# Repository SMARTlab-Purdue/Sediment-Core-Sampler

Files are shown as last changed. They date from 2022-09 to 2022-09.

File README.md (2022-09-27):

# Uncrewed Remote Underwater Robotic Sediment Core Sampler
<p align="center">
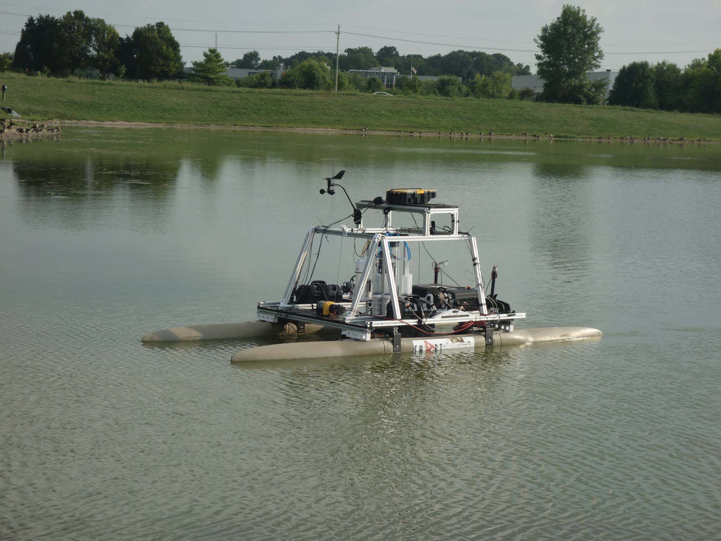
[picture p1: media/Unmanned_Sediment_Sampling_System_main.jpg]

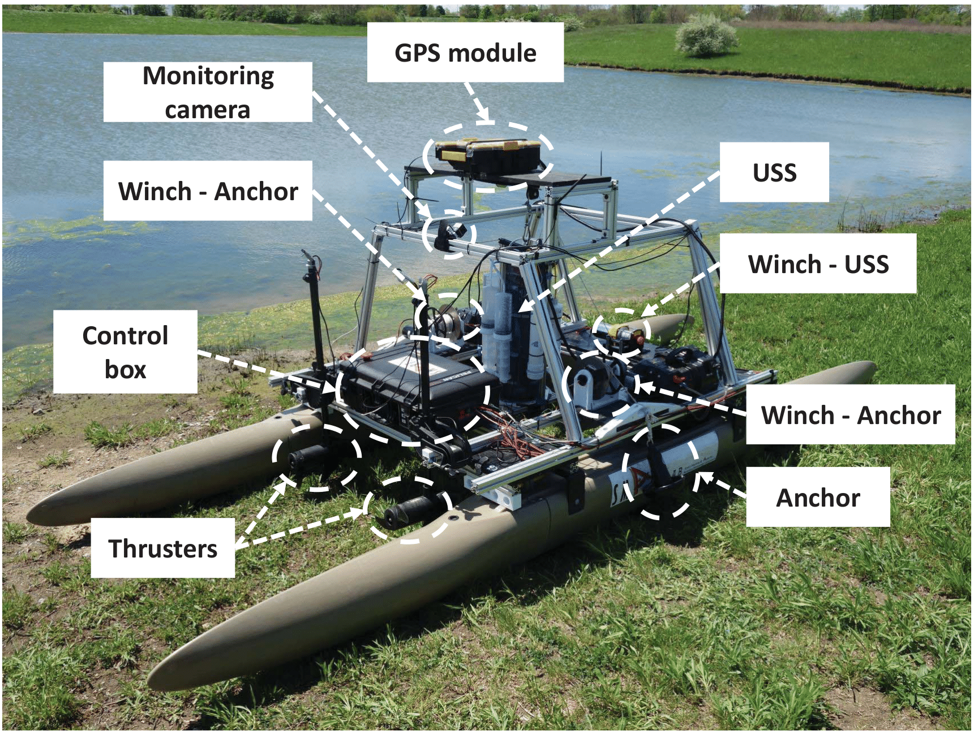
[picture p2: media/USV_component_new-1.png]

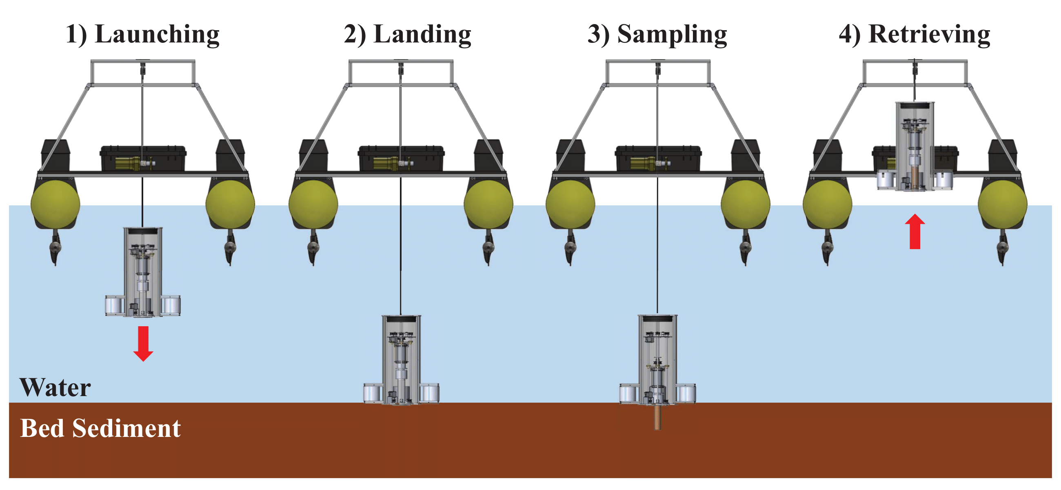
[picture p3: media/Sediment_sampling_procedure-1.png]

</p>

Sediment has a significant impact on social, economic, and environmental systems. With the need for an effective sediment management and monitoring systems growing more important, a method for precisely and reproducibly obtaining sediment samples that represent the actual environment is essential for water resource management and researchers across aquatic domains (such as lakes, rivers, reservoirs, mine drainage ponds, and wastewater lagoons). To meet this need, robotic approaches for sediment sampling have been introduced. However, they are not tailored to a sediment sampling method and do not focus on the quality of the sediment sample. In this paper, we introduce an uncrewed sediment sampling system based on the unmanned surface vehicle (USV) and underwater sediment sampler (USS) to collect sediment samples and with the ability to comprehensively study sample quality from surface-water environments. The main objective of the USV is to carry the USS to the desired sampling area and then maintain its position while launching the USS to the bottom of the body of water and sampling the sediment. The core sampling method was adopted for the USS to extend the use of the sampled sediment by minimizing the disturbance while sampling. We integrated highly flexible sediment sampling patterns and self-adaptability mechanisms to investigate the samples’ reliability and quality, and tested the effectiveness of the flexible mechanisms. Through extensive experiments, we evaluated and validated the performance of the sediment sampling system in both lab and real environments and optimized the operation of the system as a whole.

# Component List and Cost
| USV Conponent                             | Price (USD)   |
| ---------------------------------------------- | --------- |
| Nvidia Jetson Nano                             | $109.00   |
| Cytron Thruster motor driver SmartDriveDuo-30  | $150.00   |
| Two Minn kota Thrusters Model: 1352230         | $220.00   |
| Expandacraft 12 foot outrigger kit for 2 sides | $1,054.00 |
| Two tsiny DC motors for winches TS-30GZ6287    | $58.00    |
| BADLAND 2500 Lbs Utility Electric Winch        | $70.00    |
| Sparkfun Compass - HMC6352                     | $17.00    |
| Sparkfun GPS - EM506                           | $40.00    |
| USB camera ELP-USBFHD01M-L21                   | $46.00    |
| Miscellaneous                   | ~$115.00    |
| **USV Cost**                          | **$2,900.00**   |

| USS Component                                          | Price (USD) |
| ------------------------------------------------------ | ----------- |
| Two Sparkfun Pressure sensors MS5803-14BA              | $20.00      |
| testco Solenoid - 100 STA                              | $27.00      |
| Two Sparkfun Potentiometers COM-09119                  | $10.00      |
| Lipo battery 3S1P                                      | $64.00      |
| Battery volt/current sensor - Pixhawk Power Module BEC | $14.00      |
| 8'' ePlastics acrylic tube                             | $315.00     |
| Two Bluerobotics 8'' Flange WTE8-M-FLANGE-SEAL-R1-RP   | $170.00     |
| 8'' Bluerobotics cover WTE8-M-END-CAP-R1-RP            | $42.00      |
| Two Rubber bellow B01IH8JKJI                           | $40.00      |
| 3 Linear thearded rods 3313N19                         | $53.00      |
| 4 550ml syringes KIK-PLA-SYR-011                       | $56.00      |
| PVC pipes                                              | $15.00      |
| Miscellaneous                   | ~$154.00    |
| **USS Total Cost**                                         | **$1,800.00**   |
| **Platform Total Cost**                                    | **$4,700.00**   |

# Set ups

0. Set up network
 - pass: SmartROS recognizable from base station

1. main(12 V) power on; MCU 1, 2, and 3 power on
 - pass: MCU 1, 2, and 3 power/fan on

2. Nano power on
 - pass: check the green LED on

3. Arduino Mega reset
 - pass: MCU 1, 2, and 3 no blinking.
 - troubleshooting: Repeat 3 until success.

4. (from base station) ssh into nano
```
$ ssh junhan@192.168.1.4
```
 - pass: login successfully
 - troubleshooting: 192.168.1.1 -> check if nano is connected to the network; Nano's name is `junahn-desktop`

5. Sampler Controller / solenoid power on
 - pass: run the command on nano
 ```
$ ls -lha /dev/wabash_sampler
lrwxrwxrwx 1 root root 7 Mar 13 22:40 /dev/wabash_sampler -> ttyACM1
```

6. (in ssh) ros service runs okay
 - pass: the result shows Active (running)
 - troubhelshooting: sudo -i service wabashcore restart
```
$ sudo -i service wabashcore status
```
# **CHECK** If the IP address of the device changed, you have to reset the IP address.
```
$ nano setup.sh
$ source setup.sh 
```
and
```
$ systemctl status wabashcore
$ nano wabash.sh
$ sudo service wabashcore restart
```
MY_IP is the IP of the computer you run docker containers
MASTER_IP is the IP where WabashCore ROS is running (e.g., Jetson Nano) 

7. (in ssh) run source setup.sh
must run before ./run.all.sh (even if IP is not changed

8. (in ssh) launch wabash services
```
$ cd /home/junhan/repo/Codes/docker
$ ./run_all.sh
docker ps
CONTAINER ID        IMAGE               COMMAND                  CREATED             STATUS              PORTS               NAMES
97eb41a8ddde        wabash_ros          "/ros_entrypoint.sh …"   3 minutes ago       Up 3 minutes                            wabash_cam_fisheye
fb143d1255b8        wabash_ros          "/ros_entrypoint.sh …"   3 minutes ago       Up 3 minutes                            wabash_video_server
c75b6b758a35        wabash_ros          "/ros_entrypoint.sh …"   16 minutes ago      Up 16 minutes                           wabash_motor_driver
60dec6e54943        wabash_ros          "/ros_entrypoint.sh …"   16 minutes ago      Up 16 minutes                           wabash_distance_traveled
3dc0acf10f40        wabash_ros          "/ros_entrypoint.sh …"   16 minutes ago      Up 16 minutes                           wabash_solenoid_controller
191ef87043a8        wabash_ros          "/ros_entrypoint.sh …"   16 minutes ago      Up 16 minutes                           wabash_rotary_controller
1329ad7e1d2f        wabash_ros          "/ros_entrypoint.sh …"   16 minutes ago      Up 16 minutes                           wabash_sampler_serial
+ PRESSURE_DEPTH!!!
+ GPS!!!!
$ rostopic list (you should see many topics there!)
```

9. run UI on the base station
```
$ ./ui.run 192.168.1.3
$ cd /storage/
$ python3 ui.py
 - pass: you see the UI
 - troubleshooting: you may need to make the terminal full size
```

10. (in ssh) record the experiment
```
$ ./record.sh
Ctrl + C to stop
$ ls -lha 
2021-03-13-23-46-43.bag .....
```
11. (in base station) open browser (i.e. Chrome) to monitor USV via fisheye camera (use Jetson IP)

192.168.1.6:8080

12-a. (in another ssh) send out the USV manually
```
$ rosrun teleop_twist_keyboard teleop_twist_keyboard.py
```
press 'q' button to increase the speed
press 'z' button to decrease the speed
speed: 1 turn: 2 - max. performance of the thruster

12-b. (in another ssh) send out the USV in auto mode
```
$ cd /home/junhan/repo/Codes/docker/usv_autopilot
$ lat=LATITUDE lon=LONGITUDE ./auto.sh
Setting the autopilot to a coordinate: LATITUDE, LONGITUDE
+ rostopic pub -1 /usv/autopilot/cmd/engage std_msgs/Bool True
publishing and latching message for 3.0 seconds
+ rostopic pub -1 /usv/autopilot/destination sensor_msgs/NavSatFix '{latitude: LATUTUDE, longitude: LONGITUDE}'
publishing and latching message for 3.0 seconds
Done
+ set +x
```

11-c. killing autopilot in case of emergency
```
$ cd /home/junhan/repo/Codes/docker/usv_autopilot
$ ./kill.sh
Attempting to kill autopilot...
+ rostopic pub -1 /usv/autopilot/cmd/kill std_msgs/Bool True
publishing and latching message for 3.0 seconds
+ set +x
```

# How to Reset OpenCR board
```
$ rostopic pub -1 /sampler/reset std_msgs/Byte 0x00
```

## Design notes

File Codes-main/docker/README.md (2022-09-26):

## Dockerized ROS Services

To build Wabash ROS image in Docker,
```
$ ./build.sh
```

To run ROS core,
```
$ ./core.run
```

## Wabash services

To run the Wabash services,
```
# this requires the OpenCR connected
$ ./run_all.sh
```

To clean them up,
```
$ ./clean.sh
```

## Camera Streaming

To run camera streaming,
```
$ cp camera.run camera_left.run
$ nano camera_left.run
# modify IP to the IP address of the node on which core.run runs and NAME
# DEVICE should be the path of the camera (which might be mapped to /dev/wabash_cam_*
$ ./camera_left.run
```

To run web video service,
```
$ nano video_server.run
# modify IP to the IP address of the node on which core.run runs
$./video_server.run
```

On remote (base station) open a browser (Chrome is recommended) and type
```
# replace IP with the actual IP address of the core node
http://IP:8080
```

Finally, click the camera you want to open.

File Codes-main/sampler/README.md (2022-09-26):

## Sampler Firmware

[firmware.ino](firmware.ino) is the firmware for sadiment sampler board (OpenCR).

The code uses ROS topics to publish and subscribe messages. Available topics are,

- ...

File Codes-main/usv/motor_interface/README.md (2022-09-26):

# Arduino Mega for Interfacing with Motor drivers

An arduino mega is used to bridge interfaces between SmartDriveDuo-30/60 and Jetson.

## Commands
- `th [l, r] INT`: change direction/velocity of left/right thrusters
- `an [l, r] INT`: change direction/velocity of left/right anchors
- `sa [l, r] INT`: change direction/velocity of left/right sampler
__NOTE: only `r` is used__
- `cll [on, off]`: change on/off of left clutch
- `clr [on, off]`: change on/off of right clutch
- `cl [on, off]`: change on/off of sampler clutch
- `init`: send the init signal to the motor drivers

## Clutch Pins
```
uint8_t clutch_sampler_pin = 2;
uint8_t clutch_left_pin = 3;
uint8_t clutch_right_pin = 4;
```

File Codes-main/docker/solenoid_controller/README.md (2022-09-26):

# Solenoid Controller

`/sampler/cmd/solenoid`: float32 solenoid toggle interval in seconds; sending 0. to stop.

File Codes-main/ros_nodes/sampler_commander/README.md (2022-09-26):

# Sampler Commander

Sampler commander is a ROS node that takes commands from the base station. Its job is to convert high-level commands, e.g., "initiate sampler" into a corresponding set of commands that are executable by the sampler board.

## Commands

- init sampler: initializes the sampler

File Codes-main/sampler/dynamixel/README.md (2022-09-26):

# Dynamixel MX-64AR

## Modes

NOTE: [Reference](http://wiki.ros.org/dynamixel_controllers/Tutorials/SettingUpDynamixel)

Joint mode: position to given angle and hold

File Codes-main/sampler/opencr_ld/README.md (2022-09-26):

# OpenCR flashing on Jetson

Use the opencr_ld binary to flash firmware to OpenCR board

```
$ export OPENCR_PORT=/dev/ttyACM0
$ binary_arm64/opencr_ld ${OPENCR_PORT} 115200 /PATH/TO/FIRMWARE.bin 1
opencr_ld ver 1.0.4
opencr_ld_main 
>>
file name : /home/smartlab/sampler/firmware.ino.bin 
file size : 175 KB
Open port OK
Clear Buffer Start
Clear Buffer End
Board Name : OpenCR R1.0
Board Ver  : 0x17020800
Board Rev  : 0x00000000
>>
flash_erase : 0 : 1.079000 sec
flash_write : 0 : 0.995000 sec 
CRC OK 10C7CE4 10C7CE4 0.006000 sec
[OK] Download 
jump_to_fw 
jump finished
```

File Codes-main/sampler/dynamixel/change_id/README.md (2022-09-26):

# Change ID of Dynamixel

[change_id.ino](change_id.ino) changes ID of a connected Dynamixel. The new ID is in the code. The linear motion motor should be assigned ID 1 and rotation motor should be assigned ID 2.

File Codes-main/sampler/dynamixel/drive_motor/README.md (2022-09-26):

# Test Linear Dynamixel

[motor.ino](motor.ino) accepts a float value to drive Dynamixel ID 1 motor at the desired speed. The value is fed with the unit of m/s.

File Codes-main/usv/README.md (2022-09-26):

# Jetson Nano for USV

## Camera setup

```
# on sudo
$ cat /etc/udev/rules.d/10-wabash.rules 
SUBSYSTEM=="tty" ATTRS{idProduct}=="0042", ATTRS{idVendor}=="2341", ATTRS{manufacturer}=="Arduino*", SYMLINK+="wabash_motor_driver"
SUBSYSTEM=="tty" ATTRS{idProduct}=="5740", ATTRS{idVendor}=="0483", ATTRS{manufacturer}=="ROBOTIS", SYMLINK+="wabash_sampler"
SUBSYSTEM=="tty" ATTRS{idProduct}=="0043", ATTRS{idVendor}=="2341", SYMLINK+="wabash_gps"
SUBSYSTEM=="tty" ATTRS{idProduct}=="xxxx", ATTRS{idVendor}=="yyyy", SYMLINK+="wabash_pressure"

SUBSYSTEM=="video4linux", KERNEL=="video[0-9]*", ATTRS{idVendor}=="05a3", ATTRS{idProduct}=="9420", ATTRS{devpath}=="2.1", SYMLINK+="wabash_cam_left"
SUBSYSTEM=="video4linux", KERNEL=="video[0-9]*", ATTRS{idVendor}=="05a3", ATTRS{idProduct}=="9420", ATTRS{devpath}=="2.2", SYMLINK+="wabash_cam_right"
SUBSYSTEM=="video4linux", KERNEL=="video[0-9]*", ATTRS{idVendor}=="05a3", ATTRS{idProduct}=="9422", SYMLINK+="wabash_cam_fisheye_other"
SUBSYSTEM=="video4linux", KERNEL=="video[0-9]*", ATTRS{idVendor}=="32e4", ATTRS{idProduct}=="9230", SYMLINK+="wabash_cam_fisheye"
SUBSYSTEM=="video4linux", KERNEL=="video[0-9]*", ATTRS{idVendor}=="534d", ATTRS{idProduct}=="2109", SYMLINK+="wabash_cam_sampler"
(add more camera here)

sudo -i udevadm control --reload-rules 
sudo -i udevadm trigger 
ls -lh /dev/wabash*
```

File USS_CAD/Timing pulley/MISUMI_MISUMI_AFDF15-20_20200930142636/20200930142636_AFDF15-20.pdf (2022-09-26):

## Backside Tension Idler Pulley - Both Sides Bearing (MISUMI)

Part Number AFDF15-20 | 20200930142636
Type | Idlers | Belt Widt h Used(Inch)(Inch) | 0.37 in (3/8")
Belt Widt h Used(mm)(mm) | 10 | Ma t eria l | [Aluminum] Aluminum Alloy 2000 series
Surf a ce Trea t ment | Clear Anodize | O.D.(mm) | 20
Timing Pulleys/Idlers | Idlers | Bea ring Position | -
Groove Widt h W(mm) | 15 | Wit h or w/o Flange | Provided

Copyright © MISUMI Corporation All Rights Reserved.

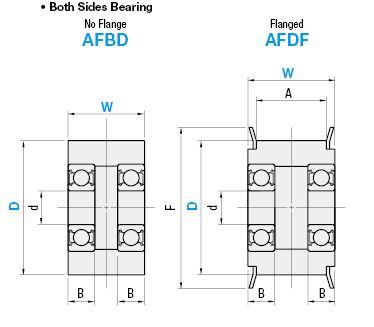
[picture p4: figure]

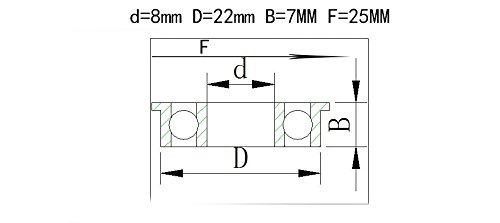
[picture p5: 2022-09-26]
USS_CAD/Ball bearing/Flange Ball Bearing F608ZZ 8x22x7 mm.jpg

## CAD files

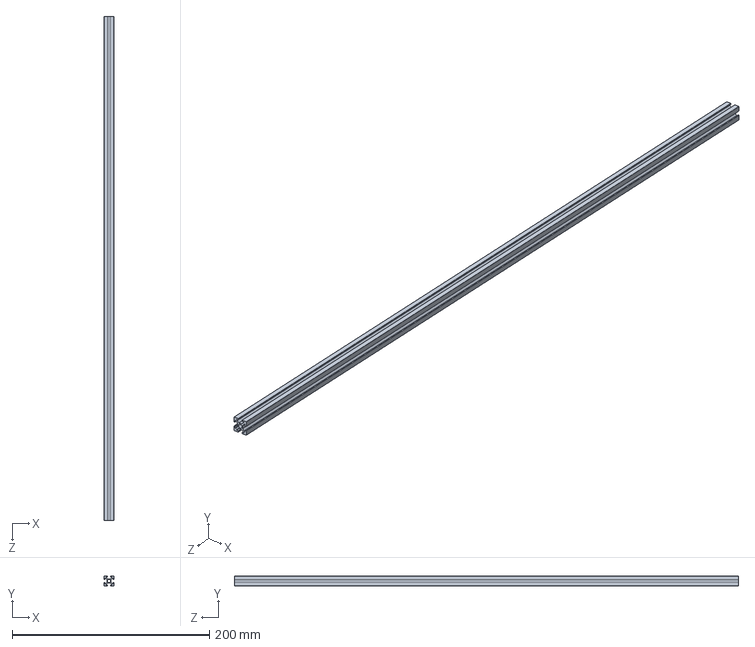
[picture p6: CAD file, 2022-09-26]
USS_CAD/Al beam_10mm_main.SLDPRT
10.0 x 10.0 x 511.0 mm

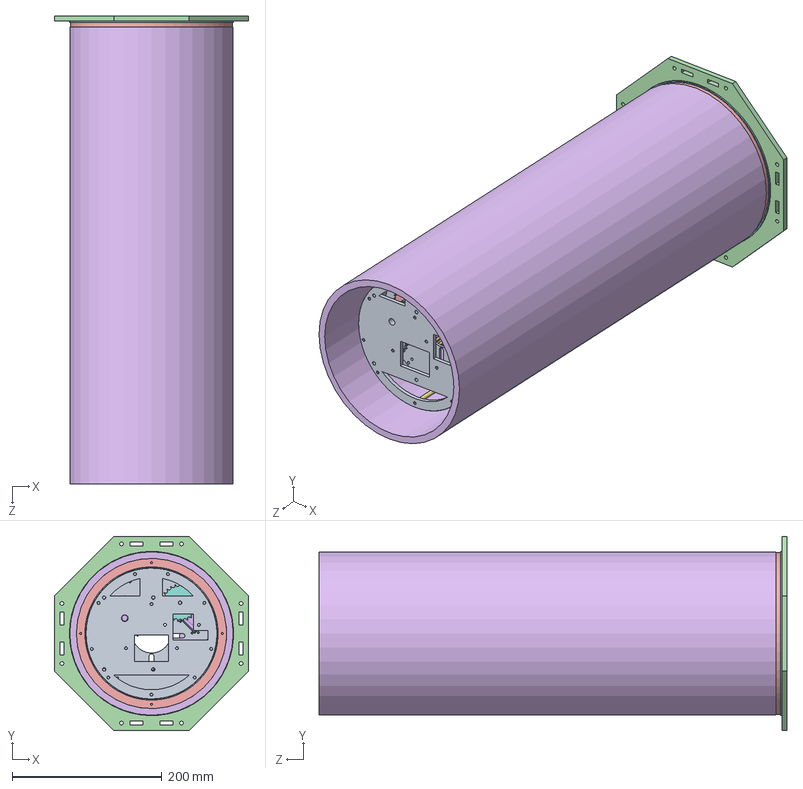
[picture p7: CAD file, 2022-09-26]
USS_CAD/Assembly/Sampler_Guide_new_2.SLDASM
259.0 x 259.0 x 624.3 mm
Top plate
Bearing mount_Top plate_new_2 x 3
8mm Lead Screw_MTSBRW8-490-F6-V6-S30-Q6 x 3
Flange Ball Bearing F608ZZ 8x22x7 mm x 2
2302K530_MACHINABLE-BORE SPROCKET
MX-64AT_AR
Timing pulley mount_MX64AR_new_3
2302K520_MACHINABLE-BORE SPROCKET
Electrics plate_new_2
Al beam_10mm_main x 3
Bearing mount_Bottom plate_new_ver.3 x 2
Bottom plate
M3x50 Spacer Round Column x 3
Rubber gasket_2mm
2302K430_MACHINABLE-BORE SPROCKET x 3
2302K430_MACHINABLE-BORE SPROCKET_8mm bore
8mm bearing mount_gear set
1mm spacer
3mm spacer
Core_Big bellow mount_bottom

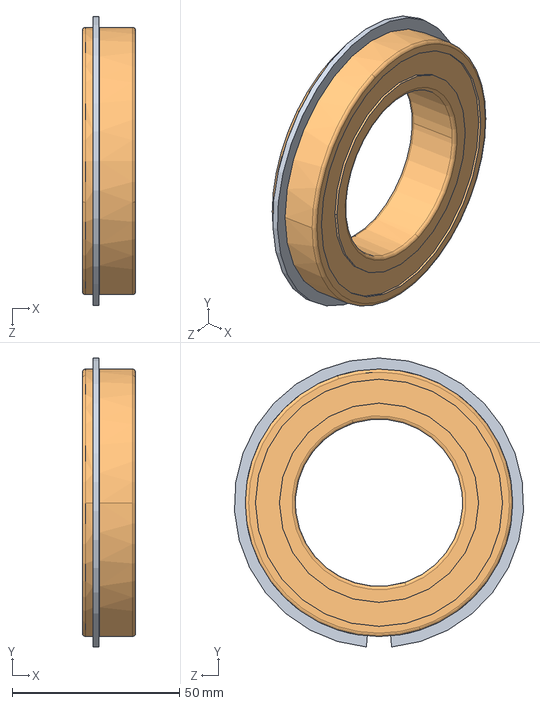
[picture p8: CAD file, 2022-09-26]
USS_CAD/Ball bearing/f608zz-flange-ball-bearing-1.snapshot.3/B6010ZZNR_SolidWorks_Native)_=2006_20200910/SOLIDWORKS/B6010ZZNR.sldasm
16.0 x 86.4 x 86.5 mm
B6010ZZNR_3
B6010ZZNR_5

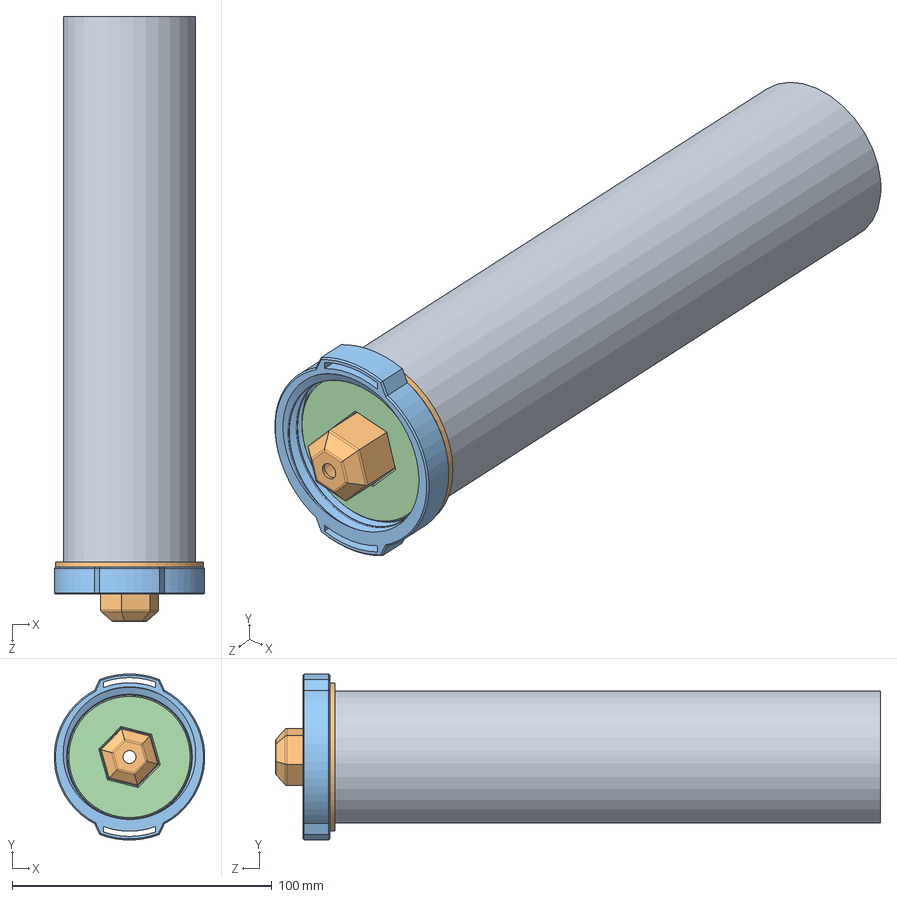
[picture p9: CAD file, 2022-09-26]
USS_CAD/Core mount/Core.SLDASM
57.9 x 63.9 x 233.0 mm
Sampling core liner
Core_Core mount_checkvv mount.stp
core core mount fastener.stp
Core_Core_mount_fastener_holder.stp

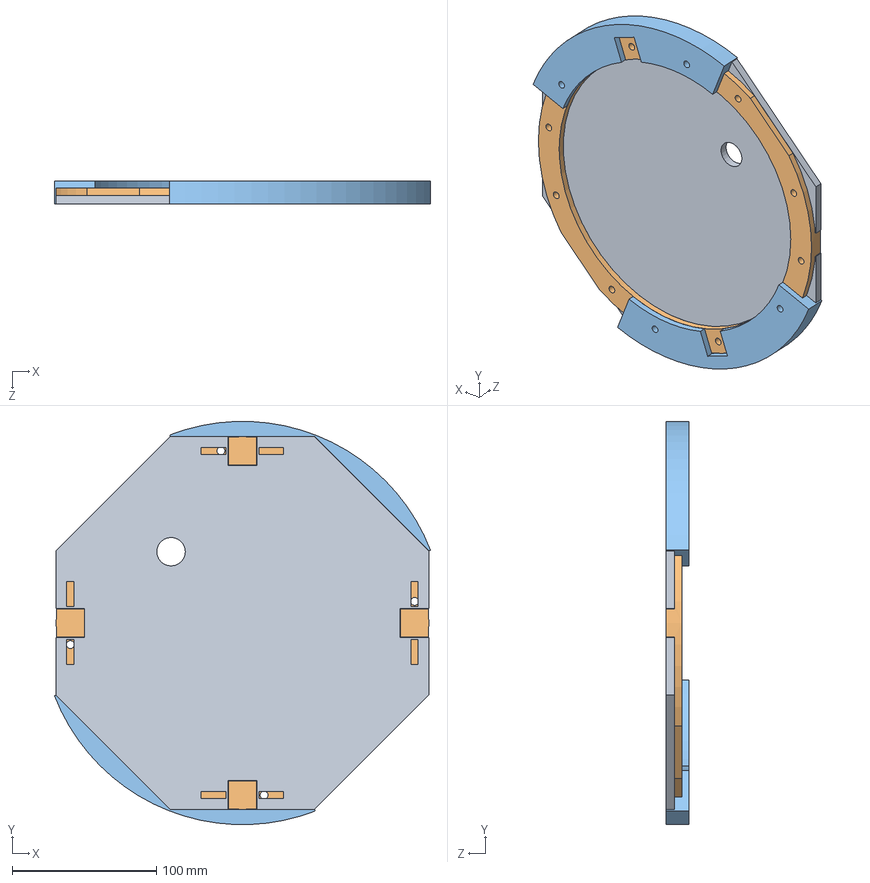
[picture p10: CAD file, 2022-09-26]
USS_CAD/External frame/External frame mount.SLDASM
261.1 x 279.8 x 16.1 mm
Top cover_2
External frame mount_ring
External frame mount_ring_parts x 2

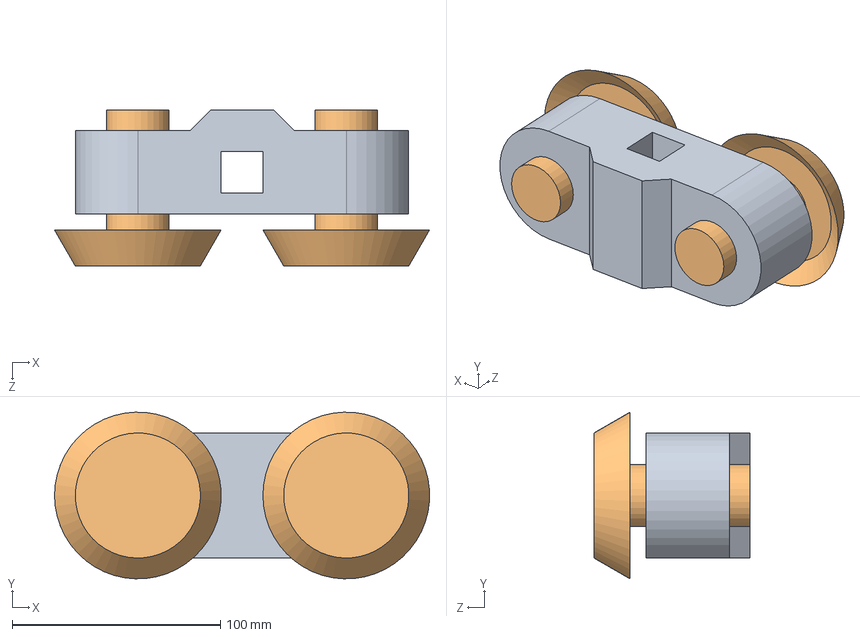
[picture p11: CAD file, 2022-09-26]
USS_CAD/Landing gear/Landing gear_concept_3.SLDASM
179.9 x 80.0 x 75.0 mm
Landing gear_concept_3_part1
Landing gear_concept_3_part2 x 2

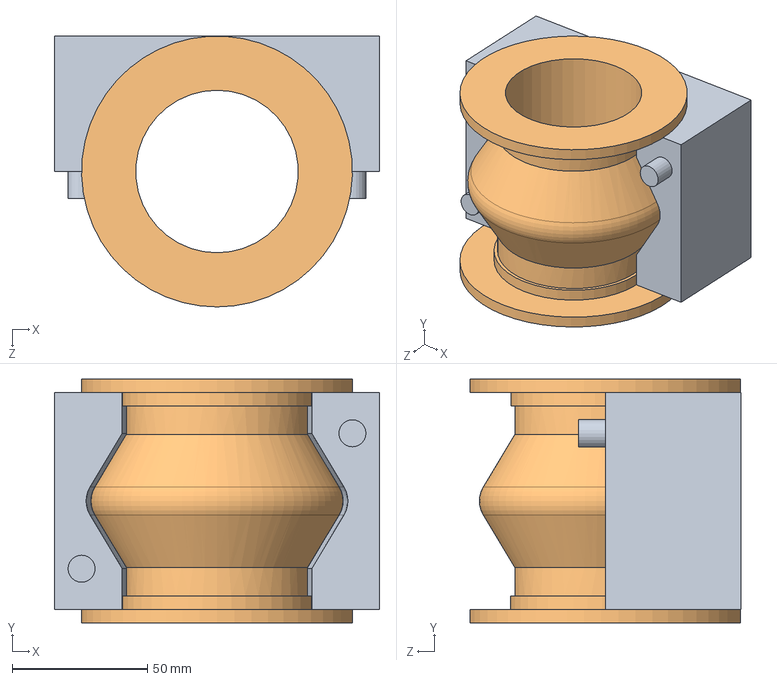
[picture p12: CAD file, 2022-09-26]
USS_CAD/Rubber bellow/Small bellow.SLDASM
120.0 x 90.0 x 100.0 mm
Small bellow mold_bottom
Small bellow mold_core

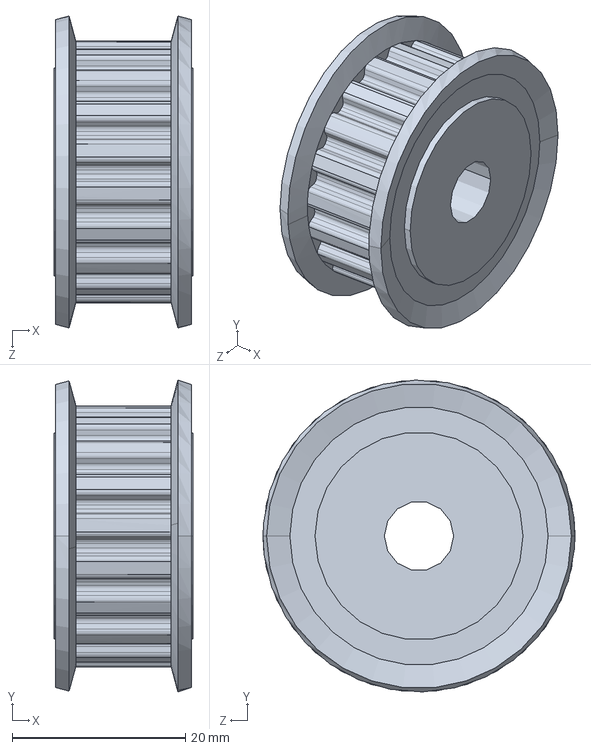
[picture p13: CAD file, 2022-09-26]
USS_CAD/Timing pulley/SOLIDWORKS/ATP19XL037_A_H8.sldasm
16.0 x 36.0 x 36.0 mm

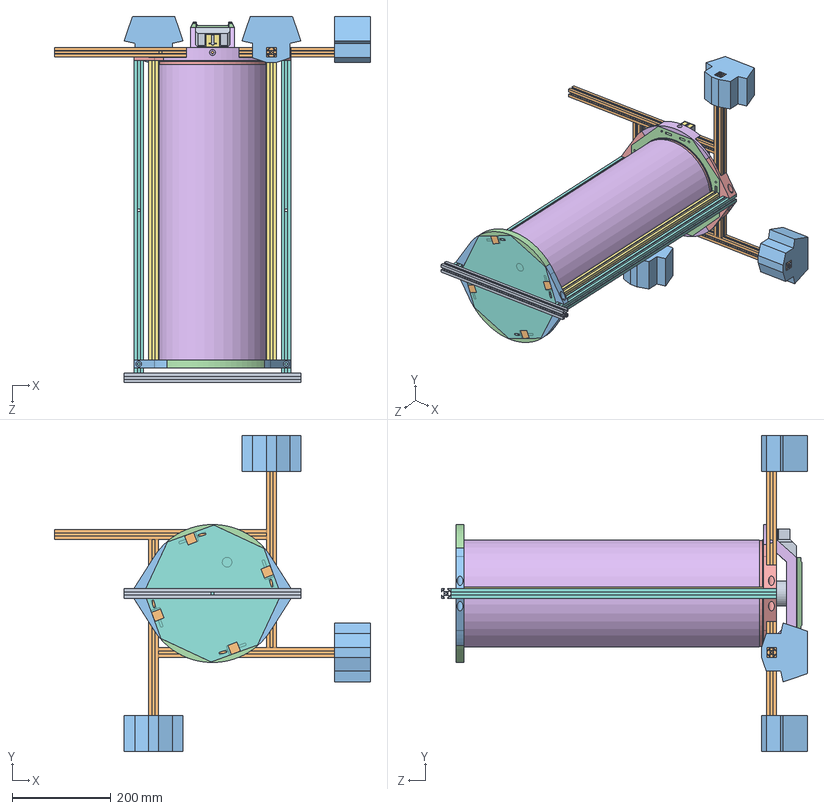
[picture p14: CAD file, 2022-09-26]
USS_CAD/Assembly/Sampler_Assemble_External Frame_properties.SLDASM
641.0 x 641.0 x 743.4 mm
Top plate
Bearing mount_Top plate_new_2 x 3
8mm Lead Screw_MTSBRW8-490-F6-V6-S30-Q6 x 3
Flange Ball Bearing F608ZZ 8x22x7 mm x 3
2302K530_MACHINABLE-BORE SPROCKET
MX-64AT_AR x 2
Timing pulley mount_MX64AR_new_3
2302K520_MACHINABLE-BORE SPROCKET
Electrics plate_new_2
Al beam_10mm_main
Bearing mount_Bottom plate_new_ver.3 x 3
Bottom plate
WTE8-M-FLANGE-SEAL-R1
8'' PVC pipe
M3x50 Spacer Round Column
Rubber gasket_2mm
2302K430_MACHINABLE-BORE SPROCKET x 3
2302K430_MACHINABLE-BORE SPROCKET_8mm bore
8mm bearing mount_gear set
1mm spacer
3mm spacer
Core_Big bellow mount_bottom
Core_Plate_new
Motor mount_core plate_rev.2
Timing pulley mount_MX64AR_new_2
2302K430_MACHINABLE-BORE SPROCKET_MX64AR
Core_Connector_top
Torque sensor_bottom
Core_Main cover_new_potentiometer
Core_Solenoid mount_potentiometer
Core_Core mount_top_potentiometer
Core_Connector_core,solenoid
Core_Core mount_bottom
1885N160_SPRING-LOADED ROTARY SHAFT SEAL
Core_Connector_bottom_b
Core_Connector_bottom_t
Core_Small bellow mount_bottom
Core_Small bellow mount_top
MTSFR8.par x 3
2302K530_MACHINABLE-BORE SPROCKET_Torque sensor
Sampling core liner
Core_Core mount_checkvv mount.stp
core core mount fastener.stp
Core_Core_mount_fastener_holder.stp
Small Bellow
Core_Big bellow mount_top
2302K430_MACHINABLE-BORE SPROCKET_idler_6mm x 2
Top cover_2 x 2
Big Bellow
External frame mount_ring
External frame mount_ring_part_2_outer frame x 2
External frame mount_ring_parts x 2
External frame mount_ring_parts_bottom mount_outer frame x 2
External frame mount_ring_parts_bottom mount x 2
Al extrusion_short x 2
Al extrusion_tall x 2
Al extrusion_top bar
Al extrusion(20x20x430) x 4
Lead mount_final x 2
gate guide.stp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

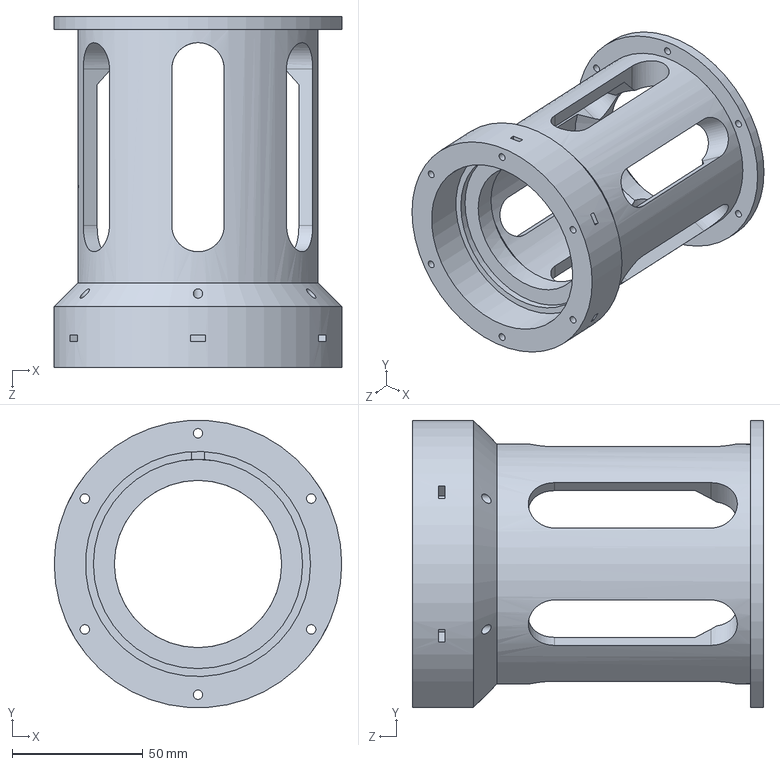
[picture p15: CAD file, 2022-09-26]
USS_CAD/Core_Main cover.SLDPRT
110.0 x 109.9 x 134.3 mm

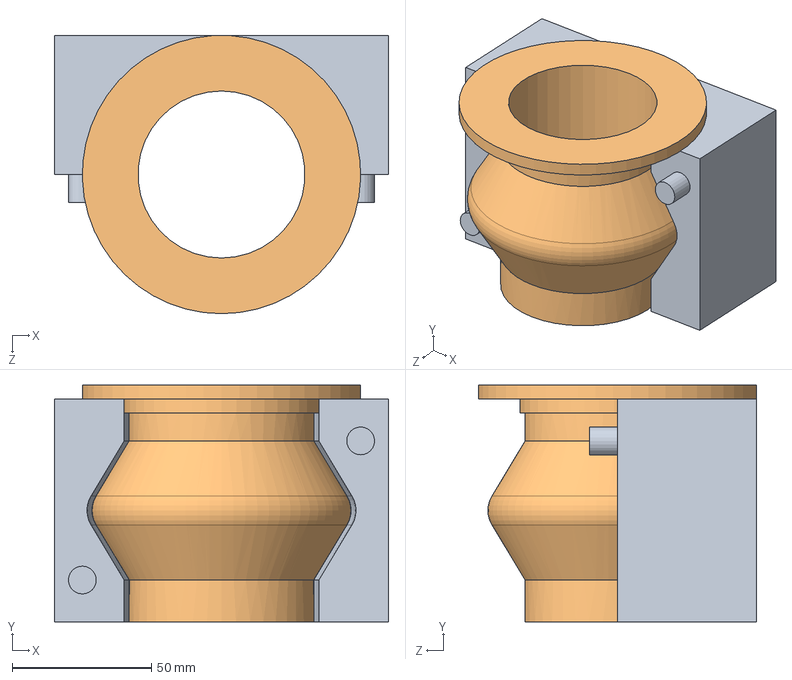
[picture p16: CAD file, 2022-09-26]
USS_CAD/Rubber bellow/Small bellow casting_2.SLDASM
120.0 x 85.0 x 100.0 mm
Small bellow mold_bottom
Small bellow mold_core_new_1

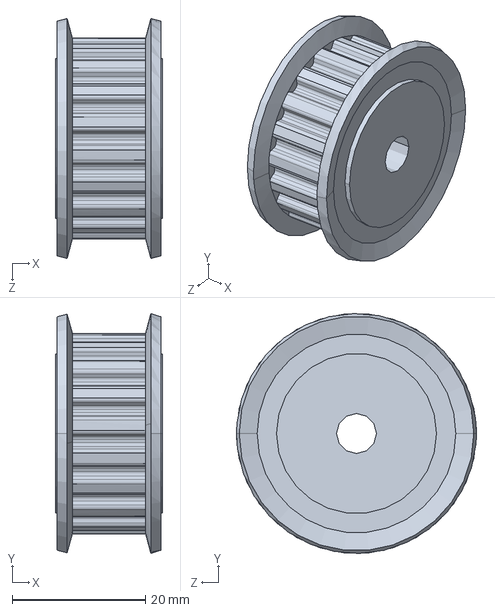
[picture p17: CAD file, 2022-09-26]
USS_CAD/Timing pulley/SOLIDWORKS/ATP19XL037_A_H6.sldasm
16.0 x 36.0 x 36.0 mm

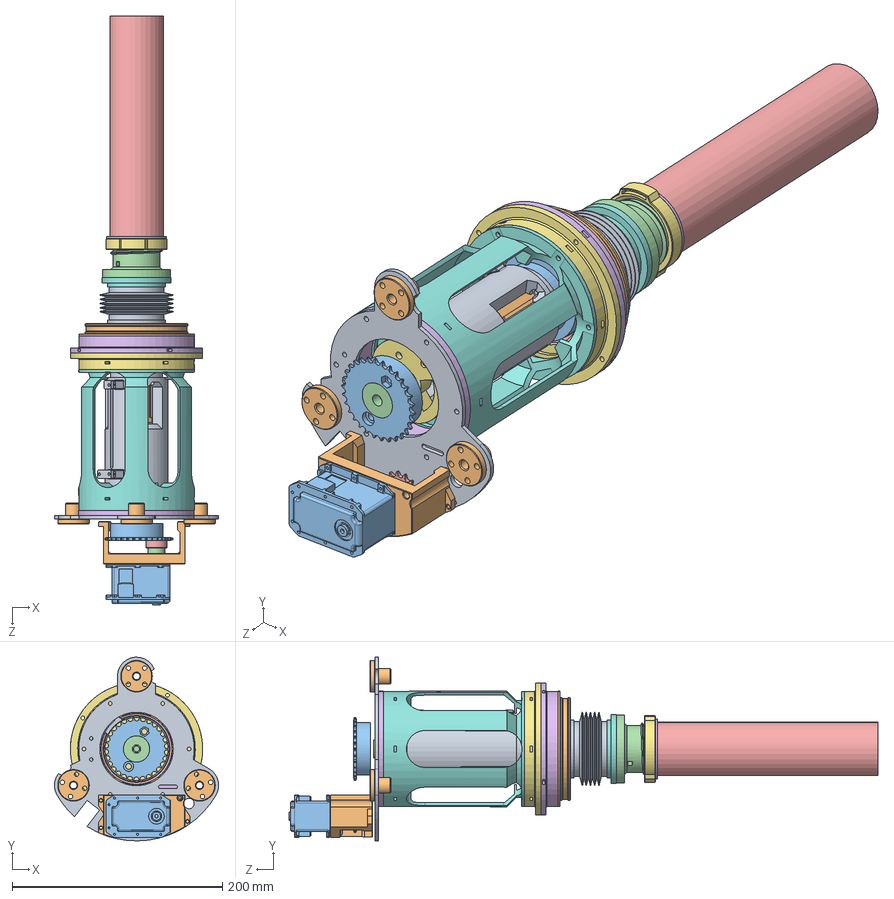
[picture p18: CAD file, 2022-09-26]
USS_CAD/Assembly/Sampler_Core_new.SLDASM
156.4 x 175.0 x 560.7 mm
Core_Plate_new
Motor mount_core plate_rev.2
MX-64AT_AR
Timing pulley mount_MX64AR_new_2
2302K430_MACHINABLE-BORE SPROCKET_MX64AR
Core_Connector_top
Torque sensor_bottom
Core_Main cover_new_potentiometer
Core_Solenoid mount_potentiometer
Core_Core mount_top_potentiometer
Core_Connector_core,solenoid
Core_Core mount_bottom
1885N160_SPRING-LOADED ROTARY SHAFT SEAL
Core_Connector_bottom_t
Core_Small bellow mount_bottom
Core_Small bellow mount_top
MTSFR8.par x 3
2302K530_MACHINABLE-BORE SPROCKET_Torque sensor
Flange Ball Bearing F608ZZ 8x22x7 mm
Sampling core liner
Core_Core mount_checkvv mount.stp
core core mount fastener.stp
Core_Core_mount_fastener_holder.stp
Small Bellow
Core_Big bellow mount_top

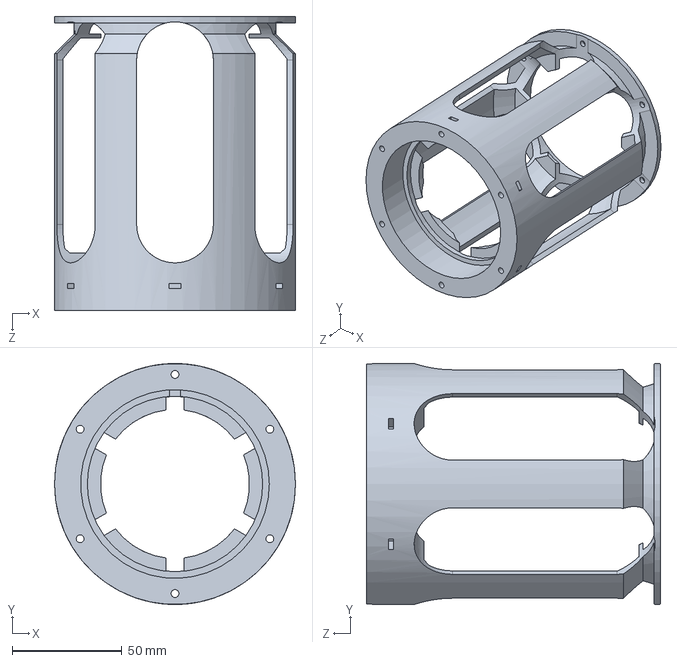
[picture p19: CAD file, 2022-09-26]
USS_CAD/Core_Main cover_new_potentiometer.SLDPRT
110.0 x 110.0 x 134.3 mm

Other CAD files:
USS_CAD/Ball bearing/B6010ZZNR_SolidWorks_Native)_=2006_20201014/SOLIDWORKS/B6010ZZNR.sldasm
USS_CAD/Timing pulley/SOLIDWORKS/ATP19XL037_A_H8_QTC16_M3.sldasm
USS_CAD/Assembly/Sampler_Assemble_External Frame.SLDASM
USS_CAD/Assembly/Sampler_Assemble.SLDASM
USS_CAD/1885N160_SPRING-LOADED ROTARY SHAFT SEAL.SLDPRT
USS_CAD/3mm spacer.SLDPRT
USS_CAD/8_ PVC pipe.SLDPRT
USS_CAD/8_ PVC pipe_property.SLDPRT
USS_CAD/8mm shaft_hollow_56.7.SLDPRT
USS_CAD/Al extrusion(20x20x150).SLDPRT
USS_CAD/Al extrusion(20x20x430).SLDPRT
USS_CAD/Al extrusion(20x20x615.6).SLDPRT
USS_CAD/Assembly/Old/MX64AR mount.SLDASM
USS_CAD/Assembly/Old/Motor unit_core plate.SLDASM
USS_CAD/Assembly/Old/Sampler_Core.SLDASM
USS_CAD/Assembly/Old/Sampler_Guide.SLDASM
USS_CAD/Assembly/Old/Sampler_Guide_new.SLDASM
USS_CAD/Assembly/Old/Sampler_Test_1.SLDASM
USS_CAD/Assembly/Old/Sampler_Test_1_1.SLDASM
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

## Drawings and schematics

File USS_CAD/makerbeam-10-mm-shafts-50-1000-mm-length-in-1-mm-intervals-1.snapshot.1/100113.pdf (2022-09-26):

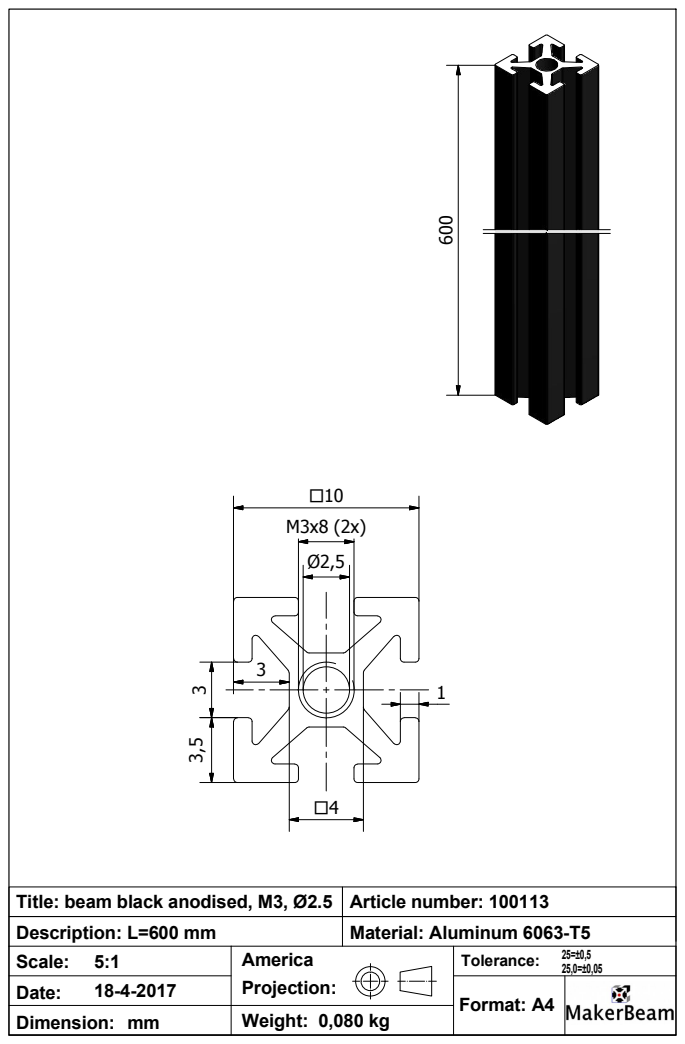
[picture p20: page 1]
America; Weight: 0,080 kg; 25=±0,5 Scale:; Date:; Dimension: mm; Format: A4; Tolerance:; Article number: 100113; Description: L=600 mm; Material: Aluminum 6063-T5; Projection:

Title: beam black anodised, M3, Ø2.5

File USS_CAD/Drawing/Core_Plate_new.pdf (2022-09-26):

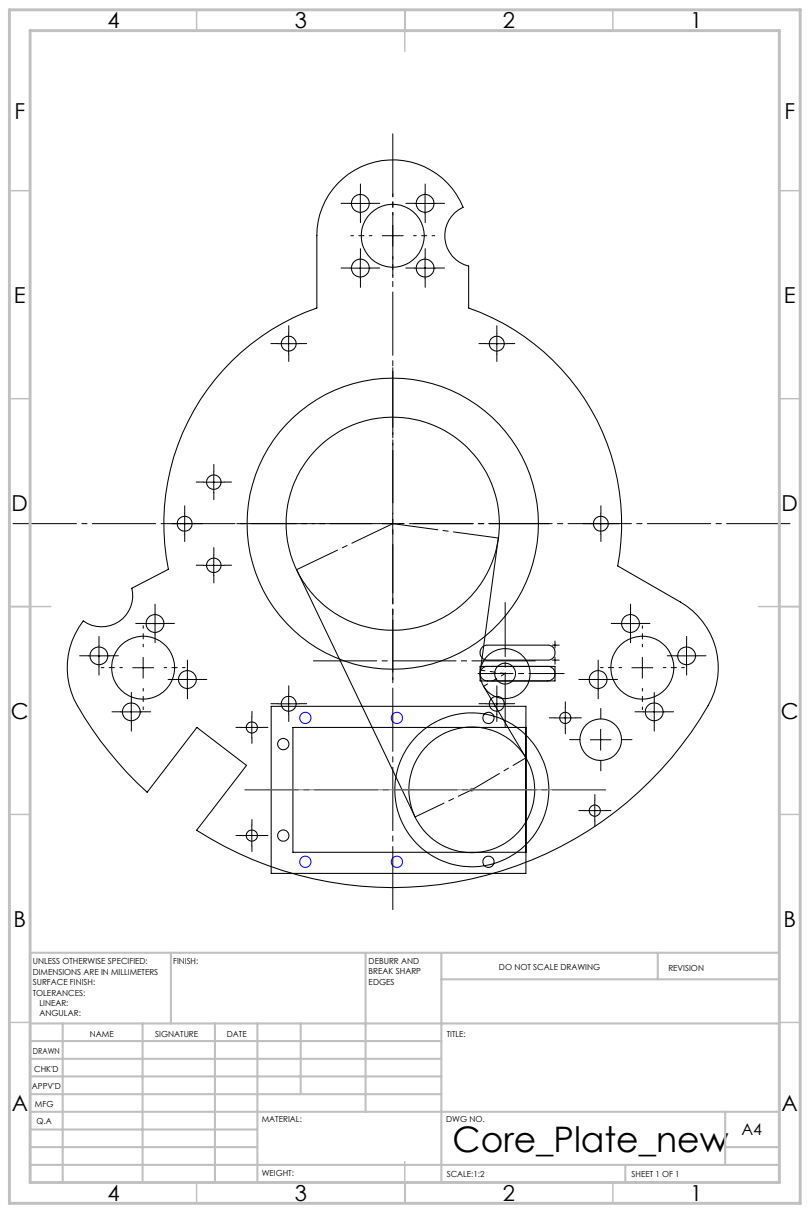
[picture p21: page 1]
FINISH:; DEBURR AND; BREAK SHARP; DO NOT SCALE DRAWING; REVISION; SCALE:1:2; SHEET 1 OF 1

UNLESS OTHERWISE SPECIFIED:
DIMENSIONS ARE IN MILLIMETERS
SURFACE FINISH:
TOLERANCES:
LINEAR:
ANGULAR:

NAME | SIGNATURE | DATE | | | | TITLE:

DRAWN
CHK'D
APPV'D
MFG
Q.A | | | | MATERIAL: | DWG NO. Core_Plate_new | A4

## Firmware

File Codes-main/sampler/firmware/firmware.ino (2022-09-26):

/*******************************************************************************
* Copyright 2016 ROBOTIS CO., LTD.
*
* Licensed under the Apache License, Version 2.0 (the "License");
* you may not use this file except in compliance with the License.
* You may obtain a copy of the License at
*
*     http://www.apache.org/licenses/LICENSE-2.0
*
* Unless required by applicable law or agreed to in writing, software
* distributed under the License is distributed on an "AS IS" BASIS,
* WITHOUT WARRANTIES OR CONDITIONS OF ANY KIND, either express or implied.
* See the License for the specific language governing permissions and
* limitations under the License.
*******************************************************************************/

/* Authors: Yoonseok Pyo, Leon Jung, Darby Lim, HanCheol Cho */


#include <ros.h>
#include <sensor_msgs/Imu.h>
#include <std_msgs/Byte.h>

#include <std_msgs/Float32.h>
#include <std_msgs/Int32.h>

#include <tf/tf.h>
#include <tf/transform_broadcaster.h>

#include <IMU.h>

#include <SPI.h>

//#include <Wire.h>
//#include <SparkFun_MS5803_I2C.h> // Click here to get the library: http://librarymanager/All#SparkFun_MS5803-14BA

//MS5803 sensor(ADDRESS_HIGH);

#include <DynamixelWorkbench.h>

#if defined(__OPENCM904__)
  #define DEVICE_NAME "3" //Dynamixel on Serial3(USART3)  <-OpenCM 485EXP
#elif defined(__OPENCR__)
  #define DEVICE_NAME ""
#endif

#define BAUDRATE  57600
#define STALL_CURRENT 4100 // Stall current mA
#define DXL_ID_1  1
#define DXL_ID_2  2

#define SPI_MAX_speed 500000
SPISettings set1(SPI_MAX_speed, MSBFIRST, SPI_MODE0);
#define SDADtransmission 0xA6
#define SDADstatus 0xF5

#define ENCODER_PIN 8
#define RESOLUTION 40

DynamixelWorkbench dxl_wb;


float DXL_ID_1_Present_Velocity = 0;
int32_t DXL_ID_1_Present_Position, DXL_ID_2_Present_Position;
float DXL_ID_1_Current, DXL_ID_2_Current;

int16_t potentiometer_linear_pin = A0;
int16_t potentiometer_rotary_pin = A2;

// Magnetic encoder linear CS pin
uint8_t encoder_linear_cs=9;
// Magnetic encoder rotary CS pin
uint8_t encoder_rotary_cs=10;

#define STRING_BUF_NUM 64
String pressure_reading[STRING_BUF_NUM];
// bool is_new_upper_pressure = false;
// bool is_new_lower_pressure = false;

//Reset pin
int Reset = 12;

// Encoder counter
unsigned long gulCount = 0;
unsigned long gulStart_Timer = 0;

// Indicators for upper and lower limit switches
uint8_t is_upper_limit_pressed = 0;
uint8_t is_lower_limit_pressed = 0;

// When upper limit switch is pressed
// stage 0: Move linear motor down at full speed for a second
// stage 1: Stop the linear motor
uint32_t emergency_upper_limit_stage1;

// When lower limit switch is pressed
// stage 0: Stage rotary motor to center and move linear motor up for a second
// stage 1: Stop the linear motor
// stage 2: Move linear motor up (to the top)
uint32_t emergency_lower_limit_stage1;
uint32_t emergency_lower_limit_stage2;


ros::NodeHandle nh;

/*******************************************/
// Publisher Parts
/*******************************************/
//Pub_MOTORS
std_msgs::Float32 dx_1_read_current_velocity_msg;
ros::Publisher pub_dx_1_velocity_read("sampler/motor/linear/read_velocity", &dx_1_read_current_velocity_msg);
std_msgs::Int32 dx_1_read_current_position_msg;
ros::Publisher pub_dx_1_position_read("sampler/motor/linear/read_position", &dx_1_read_current_position_msg);
std_msgs::Float32 dx_1_read_current_msg;
ros::Publisher pub_dx_1_current_read("sampler/motor/linear/current", &dx_1_read_current_msg);
std_msgs::Int32 dx_2_read_current_position_msg;
ros::Publisher pub_dx_2_position_read("sampler/motor/rotary/read_position", &dx_2_read_current_position_msg);
std_msgs::Float32 dx_2_read_current_msg;
ros::Publisher pub_dx_2_current_read("sampler/motor/rotary/current", &dx_2_read_current_msg);


//Pub_IMU
sensor_msgs::Imu imu_msg;
ros::Publisher imu_pub("sampler/imu", &imu_msg);
geometry_msgs::TransformStamped tfs_msg;
tf::TransformBroadcaster tfbroadcaster;
cIMU imu;

//Pub_MAGNETIC_ENCODER_LINEAR
std_msgs::Int32 mag_encoder_linear_msg;
ros::Publisher pub_mag_encoder_linear("sampler/magnetic/linear/abs_position", &mag_encoder_linear_msg);

//Pub_MAGNETIC_ENCODER_ROTARY
std_msgs::Int32 mag_encoder_rotary_msg;
ros::Publisher pub_mag_encoder_rotary("sampler/magnetic/rotary/abs_position", &mag_encoder_rotary_msg);

//Pub_POTENTIOMETER_LINEAR
std_msgs::Int32 pot_linear_msg;
ros::Publisher pub_pot_linear("sampler/potentiometer/linear", &pot_linear_msg);

//Pub_POTENTIOMETER_ROTARY
std_msgs::Int32 pot_rotary_msg;
ros::Publisher pub_pot_rotary("sampler/potentiometer/rotary", &pot_rotary_msg);

//Pub_PRESSURE
// std_msgs::Float32 pressure_upper_msg;
// ros::Publisher pub_upper_pressure_sensor("sampler/pressure/upper/pressure", &pressure_upper_msg);
// std_msgs::Float32 pressure_lower_msg;
// ros::Publisher pub_lower_pressure_sensor("sampler/pressure/lower/pressure", &pressure_lower_msg);

//Pub_TEMPERATURE_FROM_PRESSURE_SENSOR
// std_msgs::Float32 temperature_upper_msg;
// ros::Publisher pub_upper_temperature_sensor("sampler/pressure/upper/temp", &temperature_upper_msg);
// std_msgs::Float32 temperature_lower_msg;
// ros::Publisher pub_lower_temperature_sensor("sampler/pressure/lower/temp", &temperature_lower_msg);

//Pub_VOLTAGE
std_msgs::Float32 voltage_msg;
ros::Publisher pub_voltage("sampler/voltage", &voltage_msg);

//Pub_LIMIT_UPPER
std_msgs::Byte limit_upper_msg;
ros::Publisher pub_limit_upper("sampler/switch/upper", &limit_upper_msg);

//Pub_LIMIT_LOWER
std_msgs::Byte limit_lower_msg;
ros::Publisher pub_limit_lower("sampler/switch/lower", &limit_lower_msg);

//Pub_Encoder_counter
std_msgs::Int32 encoder_counter_msg;
ros::Publisher pub_encoder_counter("sampler/encoder/linear/counter", &encoder_counter_msg);


/*******************************************/
// Subscribber Parts
/*******************************************/

void dx1_write_speed( const std_msgs::Int32& dx1_write_speed_msg) {
  int32_t dx1_write_speed = dx1_write_speed_msg.data;
  // float32_t dx1_write_speed = dx1_write_speed_msg.data; // Unit is m/s
  dxl_wb.goalSpeed(DXL_ID_1,dx1_write_speed);
  // dxl_wb.goalVelocity(DXL_ID_1, dx1_write_speed);
}
ros::Subscriber<std_msgs::Int32> sub_DX1_write_speed("sampler/motor/linear/write_speed", dx1_write_speed);

void dx2_write_position( const std_msgs::Int32& dx2_write_position_msg) {
  int32_t dx2_write_position = dx2_write_position_msg.data;
  dxl_wb.goalPosition(DXL_ID_2, dx2_write_position);
}
ros::Subscriber<std_msgs::Int32> sub_DX2_write_speed("sampler/motor/rotary/write_position", dx2_write_position);

void solenoid_control( const std_msgs::Byte& solenoid_msg) {
  if (solenoid_msg.data & 1)
  {
    digitalWrite(BDPIN_GPIO_2, HIGH);
  }
  else
  {
    digitalWrite(BDPIN_GPIO_2, LOW);
  }
}
ros::Subscriber<std_msgs::Byte> sub_solenoid_control("sampler/solenoid", solenoid_control );

bool do_calibrate = false;
void imu_calibration( const std_msgs::Byte& not_used) {
  do_calibrate = true;
}
ros::Subscriber<std_msgs::Byte> sub_imu_calibration("sampler/imu/do_calibration", imu_calibration );

void reset(const std_msgs::Byte& resetbutton_msg){
  digitalWrite(Reset, LOW);
}
ros::Subscriber<std_msgs::Byte> sub_reset("sampler/reset", reset);


void setup()
{
  digitalWrite(Reset, HIGH);
  
  // Serial for Arduino micro with pressure sensors
  // Serial1.begin(9600);

  nh.initNode();

//  Serial.begin(115200);
//  while(!Serial);
//  const char* log;
//  bool result = false;
  uint16_t model_number = 0;

  //BDPIN_GPIO_1  -> limit_SW Upper //read
  //BDPIN_GPIO_3  -> limit_SW Lower //read
  //BDPIN_GPIO_2  -> solenoid 2 //read
  pinMode(BDPIN_GPIO_1, INPUT_PULLDOWN);
  pinMode(BDPIN_GPIO_3, INPUT_PULLDOWN);
  pinMode(BDPIN_GPIO_2, OUTPUT);

  pinMode(encoder_linear_cs, OUTPUT);
  pinMode(encoder_rotary_cs, OUTPUT);

  pinMode(8, INPUT_PULLDOWN);

  SPI.begin();
  SPI.setBitOrder(MSBFIRST);

  // Dynmixel Motor setting
  /****************************************/
  /***********  DYNMIXEL MOTOR  ***********/
  /****************************************/
  dxl_wb.init(DEVICE_NAME, BAUDRATE);

  dxl_wb.ping(DXL_ID_1, &model_number);
//  Serial.println("helloworld");
  dxl_wb.ping(DXL_ID_2, &model_number);
//  if (result == false) {
//     Serial.println(log);
//     Serial.println("Failed to init");
//  } else
//  {
//    Serial.println("Succeeded to ping");
//    Serial.print("id : ");
//    Serial.print(DXL_ID_2);
//    Serial.print(" model_number : ");
//    Serial.println(model_number);
//  }
//  dxl_wb.ping(DXL_ID_3, &model_number);

  dxl_wb.wheelMode(DXL_ID_1);
//  Serial.println("about to change mode");
  dxl_wb.jointMode(DXL_ID_2);
//  Serial.println("changed mode");
//  if (result == false)
//  {
//    Serial.println(log);
//  }
//  else
//  {
//    Serial.println(log);
//  }
//  dxl_wb.jointMode(DXL_ID_3);

  //attachInterrupt(digitalPinToInterrupt(ENCODER_PIN), COUNT, CHANGE);
  attachInterrupt(4, COUNT, CHANGE);


  /****************************************/
  // Publisher Parts
  /****************************************/
  nh.advertise(pub_voltage);
  nh.advertise(imu_pub);
  tfbroadcaster.init(nh);
  //buttons
  nh.advertise(pub_limit_upper);
  nh.advertise(pub_limit_lower);
  //Motors
  nh.advertise(pub_dx_1_velocity_read);
  nh.advertise(pub_dx_1_position_read);
  nh.advertise(pub_dx_2_position_read);
  nh.advertise(pub_dx_1_current_read);
  nh.advertise(pub_dx_2_current_read);
  //Magnetic encoders
  nh.advertise(pub_mag_encoder_linear);
  nh.advertise(pub_mag_encoder_rotary);
  //Potentiometers
  nh.advertise(pub_pot_linear);
  nh.advertise(pub_pot_rotary);
  //Pressure and Temperature
//  nh.advertise(pub_upper_pressure_sensor);
//  nh.advertise(pub_lower_pressure_sensor);
//  nh.advertise(pub_upper_temperature_sensor);
//  nh.advertise(pub_lower_temperature_sensor);
  nh.advertise(pub_encoder_counter);

  /****************************************/
  // Subscriber Parts
  /****************************************/
  nh.subscribe(sub_DX1_write_speed);
  nh.subscribe(sub_DX2_write_speed);
  nh.subscribe(sub_solenoid_control);
  nh.subscribe(sub_imu_calibration);
  nh.subscribe(sub_reset);
  
  imu.begin();
  delay(1000);


  /****************************************/
  // Reset OpenCR board
  /****************************************/
  //digitalWrite(Reset, HIGH);
  //delay(200); 
  pinMode(Reset, OUTPUT);     
  delay(200);

  // Initialize emergency stages
  emergency_upper_limit_stage1 = millis();
  emergency_lower_limit_stage1 = millis();
  emergency_lower_limit_stage2 = millis();
}

uint8_t val1, val2, val3;
// MSB reg: 165
// LSB reg: 0
// 19
//
// MSB bit 18
// LSB 0
// ZEROs 5
// total = 24 / 8 = 3 bytes
//
// MPC reg: 5
// Thus, we measure absolute value of 3 bytes by SDAD command.
// 23 22 21 20 19 .... 5   4 3 2 1 0
// MSB                 LSB   ZEROS
uint32_t readMagneticEncoderData(uint8_t ss)
{
  uint8_t interval = 20;
  SPI.beginTransaction(set1);
  digitalWrite(ss, LOW);
  delay(interval);
  SPI.transfer(SDADtransmission); // send command byte 151
  delay(interval);

  val1 = SPI.transfer(0x00);
  delay(interval);
  val2 = SPI.transfer(0x00);
  delay(interval);
  val3 = SPI.transfer(0x00);
  delay(interval);
  uint32_t value = (val1 << 16) | (val2 << 8) | (val3);
  value >>= 5;
  digitalWrite(ss, HIGH);
  SPI.endTransaction();
  return value;
}

void COUNT(void)
{
  gulCount++;
}

unsigned long readEncoder() {
  //unsigned long ulRPM = 0;
  //unsigned long ulTimeDif = 0;

  //detachInterrupt(digitalPinToInterrupt(ENCODER_PIN));
  detachInterrupt(4);

  //ulTimeDif = millis() - gulStart_Timer;
  //ulRPM = 60000*gulCount;
  //ulRPM = ulRPM/ulTimeDif;
  //ulRPM = ulRPM/RESOLUTION;
  //usRPM = ((60*1000*gulCount)/ulTimeDif)/RESOLUTION;
  
  unsigned long e = gulCount;
  gulCount = 0;    
  //gulStart_Timer = millis();
  //attachInterrupt(digitalPinToInterrupt(ENCODER_PIN), COUNT, CHANGE);
  attachInterrupt(4, COUNT, CHANGE);
  return e;
}
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

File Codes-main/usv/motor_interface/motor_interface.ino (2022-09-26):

uint8_t header_duo60 = 0x55;
uint8_t header_duo30 = 0x80;

// SmartDriveDuo-60 drives thrusters
// Serial1 is connected
// WARNING: Make sure the motor driver's SW004-006 are ON
uint8_t thruster_address = 0x07;

// SmartDriveDuo-30 drives winches for anchors
// Serial1 is connected
// WARNING: Make sure the motor driver's SW006 is ON
uint8_t winches_anchors_address = 0x01;

// SmartDriveDuo-30 drives winches for sampler
// Serial3 is connected
// WARNING: Make sure the motor driver's SW005 is ON
uint8_t winches_sampler_address = 0x02;

#define STRING_BUF_NUM 64
String cmd[STRING_BUF_NUM];

uint8_t packet[4];

uint8_t clutch_sampler_pin = 2;
uint8_t clutch_left_pin = 3;
uint8_t clutch_right_pin = 4;


// Left EM connections
int in1 = 8;
int in2 = 9;
// Right EM connections
int in3 = 10;
int in4 = 11;

//On-off state of EMs
bool leftEM = HIGH;
bool rightEM = HIGH;



void setup() {
  // Make clutch ON
  pinMode(clutch_sampler_pin, OUTPUT);
  pinMode(clutch_left_pin, OUTPUT);
  pinMode(clutch_right_pin, OUTPUT);
  delay(100);
  digitalWrite(clutch_sampler_pin, LOW);
  digitalWrite(clutch_left_pin, LOW);
  digitalWrite(clutch_right_pin, LOW);
  

    // Set all the motor control pins to outputs
  pinMode(in1, OUTPUT);
  pinMode(in2, OUTPUT);
  pinMode(in3, OUTPUT);
  pinMode(in4, OUTPUT);
  
  // Turn ON all EM - Initial state (to not release the anchor immediately)
  digitalWrite(in1, HIGH);
  digitalWrite(in2, HIGH);
  digitalWrite(in3, HIGH);
  digitalWrite(in4, HIGH);
  

  // put your setup code here, to run once:
  Serial.begin(115200);
  Serial1.begin(9600); // Initialize serial
  Serial2.begin(9600);
  Serial3.begin(9600);

  delay(2000); // Delay for 2 seconds.
  
  Serial1.write(header_duo60); // Dummy byte for auto baudrate.
  Serial2.write(header_duo30); // Dummy byte for auto baudrate.
  Serial3.write(header_duo30); // Dummy byte for auto baudrate.
  delay(3000); // Delay for 3 seconds.
}

void split(String data, char separator, String* temp)
{
  int cnt = 0;
  int get_index = 0;

  String copy = data;
  
  while(true)
  {
    get_index = copy.indexOf(separator);

    if(-1 != get_index)
    {
      temp[cnt] = copy.substring(0, get_index);

      copy = copy.substring(get_index + 1);
    }
    else
    {
      temp[cnt] = copy.substring(0, copy.length());
      break;
    }
    ++cnt;
  }
}

void make_packet(uint8_t motor_select, uint8_t address, uint8_t motor_speed) {
  packet[0] = header_duo60;
  packet[1] = ((motor_select & 0x01) << 3) | address;
  packet[2] = motor_speed;
  packet[3] = packet[0] + packet[1] + packet[2];
}


// turn on left EM
void left_EM_on() {
  // Turn on left EM
  digitalWrite(in1, HIGH);
  digitalWrite(in2, LOW);

  leftEM = HIGH;  //flag state EM state as ON
}

// turn off left EM
void left_EM_off() {
  if(leftEM == HIGH) {
    // reverse polarity to break "semi-permanent" magnetism
    digitalWrite(in1, LOW);
    digitalWrite(in2, HIGH);
    delay(25);
  }

  // Turn off EM
  digitalWrite(in1, LOW);
  digitalWrite(in2, LOW);

  leftEM = LOW;   //flag state EM state as OFF
}
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

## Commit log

2022-09-26 CAD files 1
    [MX64AR mount.SLDASM, Motor unit_core plate.SLDASM, Sampler_Assemble.SLDASM, Sampler_Assemble_External Frame.SLDASM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]
2022-09-26 cad 2
    [ATP19XL037_A_H6.sldasm, ATP19XL037_A_H6_3.sldprt, ATP19XL037_A_H8.sldasm, ATP19XL037_A_H8_3.sldprt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]
2022-09-26 cad 3
    [101-08-11g_24v_r15_a15.stp.SLDPRT, 3mm spacer.STL, 3mm spacer_test2.STL, Battery case mount_test1.STL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]
2022-09-26 cad 4
    [100 STA® Push DC Tubular Solenoid.SLDPRT, 100113.stp, 195207-2XX.step, 8mm Lead Screw_MTSBRW8-490-F6-V6-S30-Q6.SLDPRT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]
2022-09-26 cad 5
    [0.8mm spacer.SLDPRT, 0.8mm spacer_test1.STL, 10mm hole guide.SLDPRT, 10mm hole guide.STL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]
2022-09-26 cad 6
    [B6010ZZNR.sldasm, B6010ZZNR_3.sldprt, B6010ZZNR_5.sldprt, Flange Ball Bearing F608ZZ 8x22x7 mm.SLDPRT]
2022-09-26 cad 7
    [Idler mount_3mm.SLDPRT, Idler mount_3mm_new.SLDPRT, Idler mount_6mm.SLDPRT, Idler mount_6mm_new.SLDPRT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]
2022-09-26 cad 8
    [1885N160_SPRING-LOADED ROTARY SHAFT SEAL.SLDPRT, 3mm spacer.SLDPRT, 8_ PVC pipe.SLDPRT, 8_ PVC pipe_property.SLDPRT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]
